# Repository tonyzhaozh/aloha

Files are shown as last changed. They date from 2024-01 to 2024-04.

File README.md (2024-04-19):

# ALOHA: A Low-cost Open-source Hardware System for Bimanual Teleoperation

#### Project Website: https://tonyzhaozh.github.io/aloha/

This codebase contains implementation for teleoperation and data collection with the ALOHA hardware.
To build ALOHA, follow the [Hardware Assembly Tutorial](https://docs.google.com/document/d/1sgRZmpS7HMcZTPfGy3kAxDrqFMtNNzmK-yVtX5cKYME/edit?usp=sharing) and the quick start guide below.
To train imitation learning algorithms, you would also need to install [ACT](https://github.com/tonyzhaozh/act).

### Repo Structure
- ``config``: a config for each robot, designating the port they should bind to, more details in quick start guide.
- ``launch``: a ROS launch file for all 4 cameras and all 4 robots.
- ``aloha_scripts``: python code for teleop and data collection

## Quick start guide

### Hardware selection 

We suggest using a "heavy-duty" computer if possible. 

*In particular, at least 6 USB3 ports are needed. 4 ports for robot connections and 2 ports for cameras.* We have seen cases that a machine was not able to stably connect to all 4 robot arms simultaneously over USB, especially when USB hubs are used.

### Software selection -- OS:

Currently tested and working configurations: 
- :white_check_mark: Ubuntu 18.04 + ROS 1 noetic
- :white_check_mark: Ubuntu 20.04 + ROS 1 noetic

Ongoing testing (compatibility effort underway):
- :construction: ROS 2

### Software installation - ROS:
1. Install ROS and interbotix software following https://docs.trossenrobotics.com/interbotix_xsarms_docs/
2. This will create the directory ``~/interbotix_ws`` which contains ``src``.
3. git clone this repo inside ``~/interbotix_ws/src``
4. ``source /opt/ros/noetic/setup.sh && source ~/interbotix_ws/devel/setup.sh``
5. ``sudo apt-get install ros-noetic-usb-cam && sudo apt-get install ros-noetic-cv-bridge``
6. run ``catkin_make`` inside ``~/interbotix_ws``, make sure the build is successful
7. go to ``~/interbotix_ws/src/interbotix_ros_toolboxes/interbotix_xs_toolbox/interbotix_xs_modules/src/interbotix_xs_modules/arm.py``, find function ``publish_positions``.
   Change ``self.T_sb = mr.FKinSpace(self.robot_des.M, self.robot_des.Slist, self.joint_commands)`` to ``self.T_sb = None``.
   This prevents the code from calculating FK at every step which delays teleoperation.
### Hardware installation:

The goal of this section is to run ``roslaunch aloha 4arms_teleop.launch``, which starts
communication with 4 robots and 4 cameras. It should work after finishing the following steps:

Step 1: Connect 4 robots to the computer via USB, and power on. *Do not use extension cable or usb hub*.
- To check if the robot is connected, install dynamixel wizard [here](https://emanual.robotis.com/docs/en/software/dynamixel/dynamixel_wizard2/)
- Dynamixel wizard is a very helpful debugging tool that connects to individual motors of the robot. It allows
things such as rebooting the motor (very useful!), torque on/off, and sending commands.
However, it has no knowledge about the kinematics of the robot, so be careful about collisions.
The robot *will* collapse if motors are torque off i.e. there is no automatically engaged brakes in joints.
- Open Dynamixel wizard, go into ``options`` and select:
  - Protocal 2.0
  - All ports
  - 1000000 bps
  - ID range from 0-10
- Note: repeat above everytime before you scan.
- Then hit ``Scan``. There should be 4 devices showing up, each with 9 motors.

- One issue that arises is the port each robot binds to can change over time, e.g. a robot that
is initially ``ttyUSB0`` might suddenly become ``ttyUSB5``. To resolve this, we bind each robot to a fixed symlink
port with the following mapping:
  - ``ttyDXL_master_right``: right master robot (master: the robot that the operator would be holding)
  - ``ttyDXL_puppet_right``: right puppet robot (puppet: the robot that performs the task)
  - ``ttyDXL_master_left``: left master robot
  - ``ttyDXL_puppet_left``: left puppet robot
- Take ``ttyDXL_master_right``: right master robot as an example:
  1. Find the port that the right master robot is currently binding to, e.g. ``ttyUSB0``
  2. run ``udevadm info --name=/dev/ttyUSB0 --attribute-walk | grep serial`` to obtain the serial number. Use the first one that shows up, the format should look similar to ``FT6S4DSP``.
  3. ``sudo vim /etc/udev/rules.d/99-fixed-interbotix-udev.rules`` and add the following line: 

         SUBSYSTEM=="tty", ATTRS{serial}=="<serial number here>", ENV{ID_MM_DEVICE_IGNORE}="1", ATTR{device/latency_timer}="1", SYMLINK+="ttyDXL_master_right"

  4. This will make sure the right master robot is *always* binding to ``ttyDXL_master_right``
  5. Repeat with the rest of 3 arms.
- To apply the changes, run ``sudo udevadm control --reload && sudo udevadm trigger``
- If successful, you should be able to find ``ttyDXL*`` in your ``/dev``

Step 2: Set max current for gripper motors
- Open Dynamixel Wizard, and select the wrist motor for puppet arms. The name of it should be ```[ID:009] XM430-W350```
- Tip: the LED on the base of robot will flash when it is talking to Dynamixel Wizard. This will help determine which robot is selected. 
- Find ``38 Current Limit``, enter ``200``, then hit ``save`` at the bottom.
- Repeat this for both puppet robots.
- This limits the max current through gripper motors, to prevent overloading errors.

Step 3: Setup 4 cameras
- You may use usb hub here, but *maximum 2 cameras per hub for reasonable latency*.
- To make sure all 4 cameras are binding to a consistent port, similar steps are needed.
- Cameras are by default binding to ``/dev/video{0, 1, 2...}``, while we want to have symlinks ``{CAM_RIGHT_WRIST, CAM_LEFT_WRIST, CAM_LOW, CAM_HIGH}``
- Take ``CAM_RIGHT_WRIST`` as an example, and let's say it is now binding to ``/dev/video0``. run ``udevadm info --name=/dev/video0 --attribute-walk | grep serial`` to obtain it's serial. Use the first one that shows up, the format should look similar to ``0E1A2B2F``.
- Then ``sudo vim /etc/udev/rules.d/99-fixed-interbotix-udev.rules`` and add the following line 

      SUBSYSTEM=="video4linux", ATTRS{serial}=="<serial number here>", ATTR{index}=="0", ATTRS{idProduct}=="085c", ATTR{device/latency_timer}="1", SYMLINK+="CAM_RIGHT_WRIST"

- Repeat this for ``{CAM_LEFT_WRIST, CAM_LOW, CAM_HIGH}`` in additional to ``CAM_RIGHT_WRIST``
- To apply the changes, run ``sudo udevadm control --reload && sudo udevadm trigger``
- If successful, you should be able to find ``{CAM_RIGHT_WRIST, CAM_LEFT_WRIST, CAM_LOW, CAM_HIGH}`` in your ``/dev``

At this point, have a new terminal
    
    conda deactivate # if conda shows up by default
    source /opt/ros/noetic/setup.sh && source ~/interbotix_ws/devel/setup.sh
    roslaunch aloha 4arms_teleop.launch

If no error message is showing up, the computer should be successfully connected to all 4 cameras and all 4 robots.

#### Trouble shooting
- Make sure Dynamixel Wizard is disconnected, and no app is using webcam's stream. It will prevent ROS from connecting to
these devices.

### Software installation - Conda:

    conda create -n aloha python=3.8.10
    conda activate aloha
    pip install torchvision
    pip install torch
    pip install pyquaternion
    pip install pyyaml
    pip install rospkg
    pip install pexpect
    pip install mujoco==2.3.7
    pip install dm_control==1.0.14
    pip install opencv-python
    pip install matplotlib
    pip install einops
    pip install packaging
    pip install h5py

### Testing teleoperation

**Notice**: Before running the commands below, be sure to place all 4 robots in their sleep positions, and open master robot's gripper. 
All robots will rise to a height that is easy for teleoperation.

    # ROS terminal
    conda deactivate
    source /opt/ros/noetic/setup.sh && source ~/interbotix_ws/devel/setup.sh
    roslaunch aloha 4arms_teleop.launch
    
    # Right hand terminal
    conda activate aloha
    cd ~/interbotix_ws/src/aloha/aloha_scripts
    python3 one_side_teleop.py right
    
    # Left hand terminal
    conda activate aloha
    cd ~/interbotix_ws/src/aloha/aloha_scripts
    python3 one_side_teleop.py left

The teleoperation will start when the master side gripper is closed.

## Example Usages

To set up a new terminal, run:

    conda activate aloha
    cd ~/interbotix_ws/src/aloha/aloha_scripts

The ``one_side_teleop.py`` we ran is for testing teleoperation and has no data collection. To collect data for an episode, run:

    python3 record_episodes.py --dataset_dir <data save dir> --episode_idx 0

This will store a hdf5 file at ``<data save dir>``.
To change episode length and other params, edit ``constants.py`` directly.

To visualize the episode collected, run:

    python3 visualize_episodes.py --dataset_dir <data save dir> --episode_idx 0

To replay the episode collected with real robot, run:

    python3 replay_episodes.py --dataset_dir <data save dir> --episode_idx 0

To lower 4 robots before e.g. cutting off power, run:

    python3 sleep.py

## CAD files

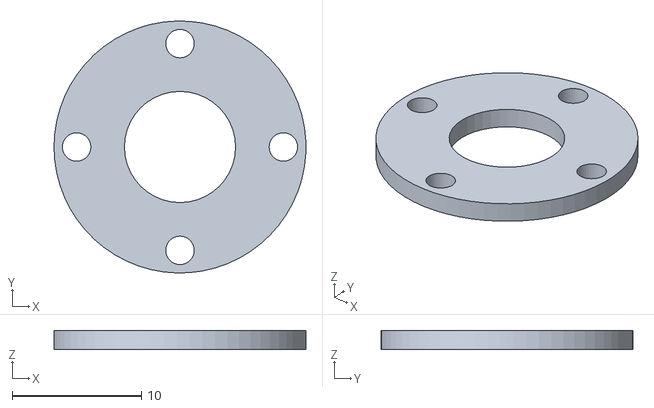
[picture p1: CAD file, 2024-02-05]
aloha2/Shim_rotor_v1.STL
19.5 x 19.5 x 1.50

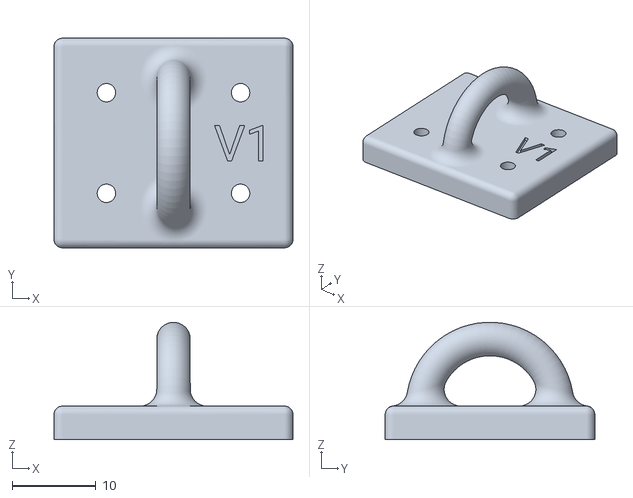
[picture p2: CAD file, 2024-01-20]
aloha2/Gravity compensator clip, elbow mount.stl
28.5 x 25.0 x 14.0

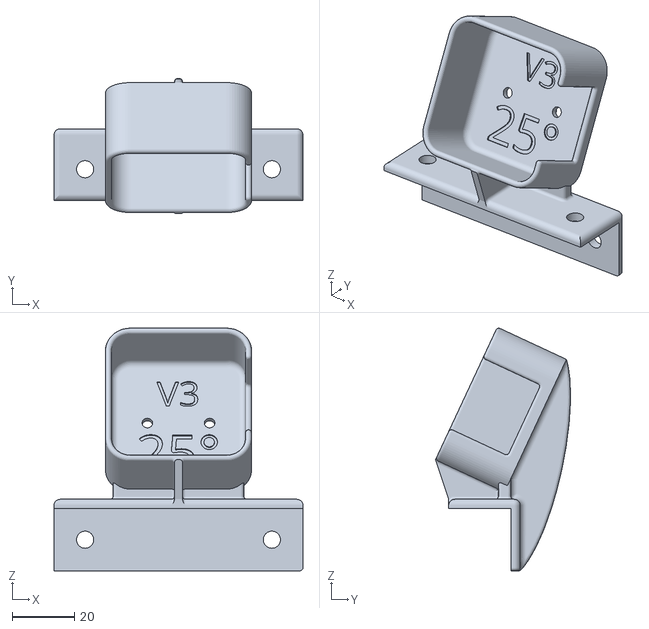
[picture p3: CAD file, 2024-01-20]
aloha2/RSd405 2020 Overhead Cam Mount v3.stl
80.0 x 43.4 x 78.0

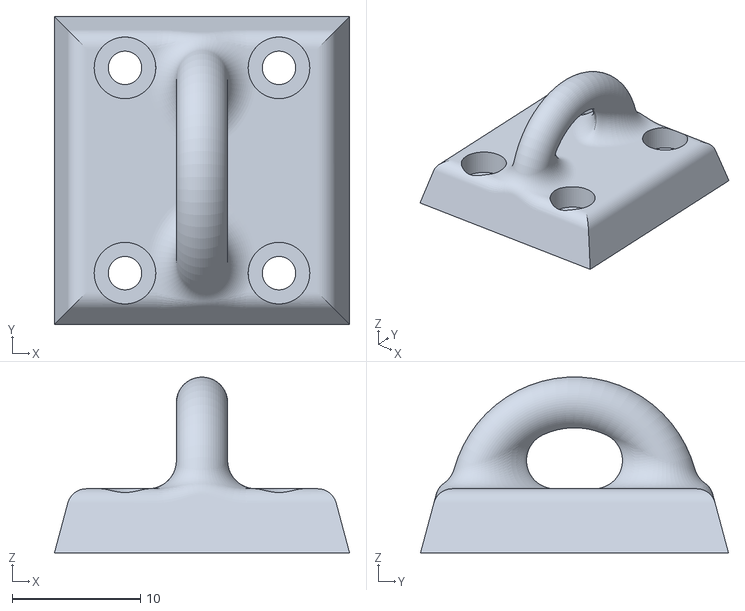
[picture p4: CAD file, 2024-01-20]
aloha2/Gravity compensator clip, wrist mount.stl
23.0 x 24.0 x 13.7

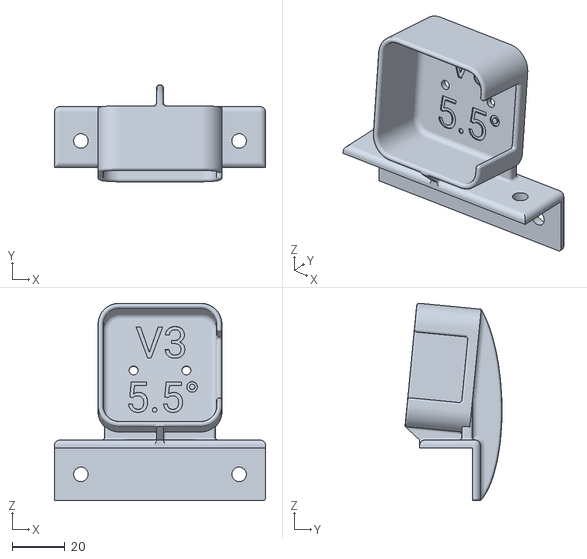
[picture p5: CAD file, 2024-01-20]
aloha2/RSd405 2020 Worms-eye Cam Mount v3.stl
80.0 x 36.8 x 74.9

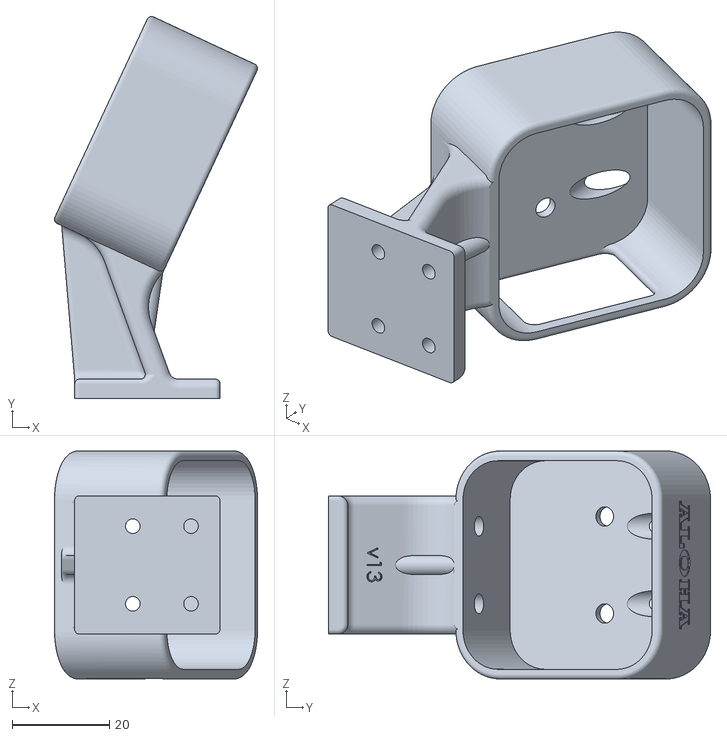
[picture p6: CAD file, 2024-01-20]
aloha2/Aloha cam wrist mount v13.stl
41.9 x 78.8 x 47.0

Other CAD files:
aloha2/W-shim_rotor_v1.STL

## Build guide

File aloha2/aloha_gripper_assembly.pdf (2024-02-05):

# Aloha Gripper Assembly

Version | Date | Author(s) | Description
1.0 | 07/28/23 | Thinh Nguyen

# 1.0 Overview

- This document outlines the steps involved in building the Aloha Gripper.

# 2.0 Parts

WidowX Gripper

Line | Part Description | Supplier | Part # | Qty
1 | W-bridge_rails_support_v1 | STEP FILE | | 1
2 | W-finger_adaptor_v1 | STEP FILE | | 2
3 | W-finger_holder_M_v1 | STEP FILE | | 1
4 | W-gripper_backplate_v1 (acrylic 3mm thickness) | STEP FILE | | 1
5 | W-hand_holder_v1 | STEP FILE | | 1
6 | W-rotor_arm_v1 | STEP FILE | | 2
7 | W-rotor_v1 | STEP FILE | | 1
8 | W-shim_rotor_v1 | STEP FILE | | 1
9 | 6725K27_5 mm Wide x 120 mm Long Rail Ball Bearing Carriage | McMaster | 6725K23 (https://www.mcmaster.com/6725K23-6725K27/) | 1
10 | 8438K1_Corrosion-Resistant Ball Bearing Carriage | McMaster | 8438K1 (https://www.mcmaster.com/8438K1/) | 4
11 | Deep Groove Ball Bearing (3mmx6mmx2.5mm) | Amazon | Amazon (https://www.amazon.com/gp/product/B075CMRGY6/ref=ppx_yo_dt_b_asin_image_o01_s00?ie=UTF8&psc=1) | 6
12 | M2 Brass Male-Female / Female-Female | Amazon | Amazon (https://www.amazon.com/gp/product/B07ZSZW8T1/ref=ppx_yo_dt_b_asin_title_o05_s00?ie=UTF8&psc=1) | 1
13 | Flat Head Screw M3 x 0.5 mm Thread, 10 mm Long | McMaster | 92125A130 (https://www.mcmaster.com/92125A130/) | 4
14 | Flat Head Screw M3 x 0.5 mm Thread, 20 mm Long | McMaster | 92125A136 (https://www.mcmaster.com/92125A136/) | 2
15 | Flat Head Screw M2 x 0.4 mm Thread, 10 mm Long | McMaster | 92010A005 (https://www.mcmaster.com/92010A005/) | 22

16 | Flat Head Screw M2 x 0.4 mm Thread, 16 mm Long | McMaster | 92010A008 (https://www.mcmaster.com/92010A008/) | 4
17 | Flat Head Screw M2 x 0.4 mm Thread, 20 mm Long | McMaster | 92095A106 (https://www.mcmaster.com/92095A106/) | 6
18 | Socket Head Screw M2 x 0.4 mm Thread, 6 mm Long | McMaster | 91292A831 (https://www.mcmaster.com/91292A831/) | 2
19 | Hex Nut M2 x 0.4 mm Thread | McMaster | 91828A111 (https://www.mcmaster.com/91828A111/) | 16
20 | Flat Head Screw M2.5 x 0.45 mm Thread, 16 mm Long | McMaster | 93395A185 (https://www.mcmaster.com/93395A185/) | 4
21 | Steel Washer for M2 Screw Size, 2.200 mm ID, 4.500 mm OD | McMaster | 98688A110 (https://www.mcmaster.com/98688A110/) | 8
22 | Short profile button head m2 x6mm (come with rails) | | | 8
23 | M3 Steel Nylon-Insert Locknut | McMaster | 90576A102 (https://www.mcmaster.com/90576A102/) | 2
24 | Socket Head Screw M2.5 x 0.45 mm Thread, 8 mm Long | McMaster | 91292A012 (https://www.mcmaster.com/91292A012/) | 8

Viper Gripper

Line | Part Description | Supplier | Part # | Qty
1 | Bridge_rails_support_v1 | STEP FILE | | 1
2 | Finger_adaptor_v1 | STEP FILE | | 2
3 | Finger_v1 | STEP FILE | | 1
4 | Gripper_backplate_v1(acrylic 3mm thickness) | STEP FILE | | 1
5 | Rotor_arm_v1 | STEP FILE | | 2
6 | Rotor_v1 | STEP FILE | | 1
7 | Shim_rotor_v1 | STEP FILE | | 1
8 | 6725K27_5 mm Wide x 150 mm Long Rail Ball Bearing Carriage | McMaster | 6725K23 (https://www.mcmaster.com/6725K23-6725K28/) | 1
9 | 8438K1_Corrosion-Resistant Ball Bearing Carriage | McMaster | 8438K1 (https://www.mcmaster.com/8438K1/) | 4
10 | Deep Groove Ball Bearing (3mmx6mmx2.5mm) | Amazon | Amazon (https://www.amazon.com/gp/product/B075CMRGY6/ref=ppx_yo_dt_b_asin_image_o01_s00?ie=UTF8&psc=1) | 6
11 | M2 Brass Male-Female / Female-Female | Amazon | Amazon (https://www.amazon.com/gp/product/B07ZSZW8T1/ref=ppx_yo_dt_b_asin_title_o05_s00?ie=UTF8&psc=1) | 1
12 | Flat Head Screw M3 x 0.5 mm Thread, 10 mm Long | McMaster | 92125A130 (https://www.mcmaster.com/92125A130/) | 4
13 | Flat Head Screw M3 x 0.5 mm Thread, 20 mm Long | McMaster | 92125A136 (https://www.mcmaster.com/92125A136/) | 2
14 | Flat Head Screw M2 x 0.4 mm Thread, 10 mm Long | McMaster | 92010A005 (https://www.mcmaster.com/92010A005/) | 22
15 | Flat Head Screw M2 x 0.4 mm Thread, 16 mm Long | McMaster | 92010A008 (https://www.mcmaster.com/92010A008/) | 4
16 | Flat Head Screw M2 x 0.4 mm Thread, 20 mm Long | McMaster | 92095A106 (https://www.mcmaster.com/92095A106/) | 6
17 | Socket Head Screw M2 x 0.4 mm Thread, 6 mm Long | McMaster | 91292A831 (https://www.mcmaster.com/91292A831/) | 2
18 | Hex Nut M2 x 0.4 mm Thread | McMaster | 91828A111 (https://www.mcmaster.com/91828A111/) | 16
19 | Flat Head Screw M2.5 x 0.45 mm Thread, 16 mm Long | McMaster | 93395A185 (https://www.mcmaster.com/93395A185/) | 4
20 | Steel Washer for M2 Screw Size, 2.200 mm ID, 4.500 mm OD | McMaster | 98688A110 (https://www.mcmaster.com/98688A110/) | 8
21 | Short profile button head m2 x6mm (come with rails) | | | 8
22 | M3 Steel Nylon-Insert Locknut | McMaster | 90576A102 (https://www.mcmaster.com/90576A102/) | 2

# 3.0 Assembly

## 3.1 Mechanical

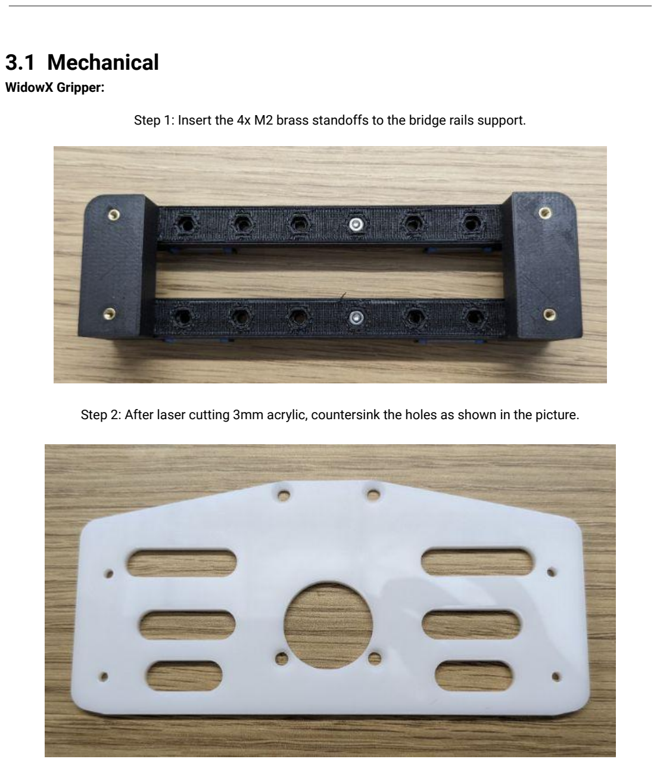
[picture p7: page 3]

WidowX Gripper:

Step 1: Insert the 4x M2 brass standoffs to the bridge rails support.
Step 2: After laser cutting 3mm acrylic, countersink the holes as shown in the picture.

Step 3: Install the 3 bearings on the rotor arm (2 on the right side and 1 on the left side).

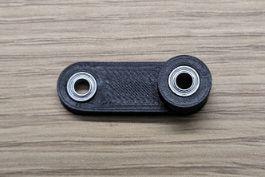
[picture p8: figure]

Step 4: Use a tap to create M3 threads in the middle holes, to a depth of about 5mm.

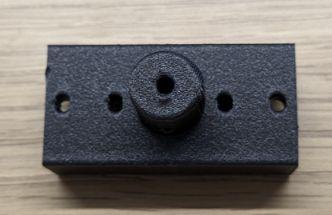
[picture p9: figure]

Step 5: Attach the rotor and rotor arm together with an M3x10mm countersunk screw and lock nut, as shown in the figure.

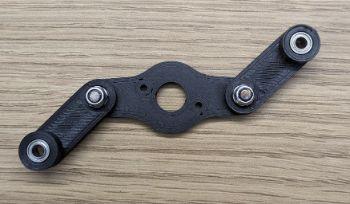
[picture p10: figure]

Step 6: Attach the rails with carriages to the bridge, and secure them with M2x16mm countersunk screws at both ends. Use M2 x 10mm countersunk screws and nuts to secure the middle holes.

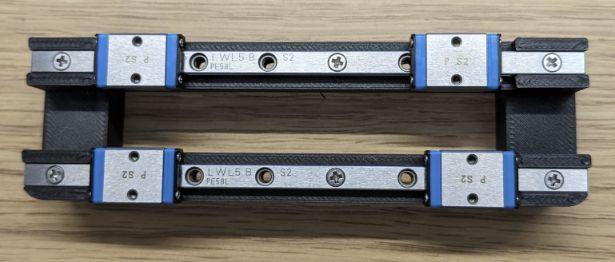
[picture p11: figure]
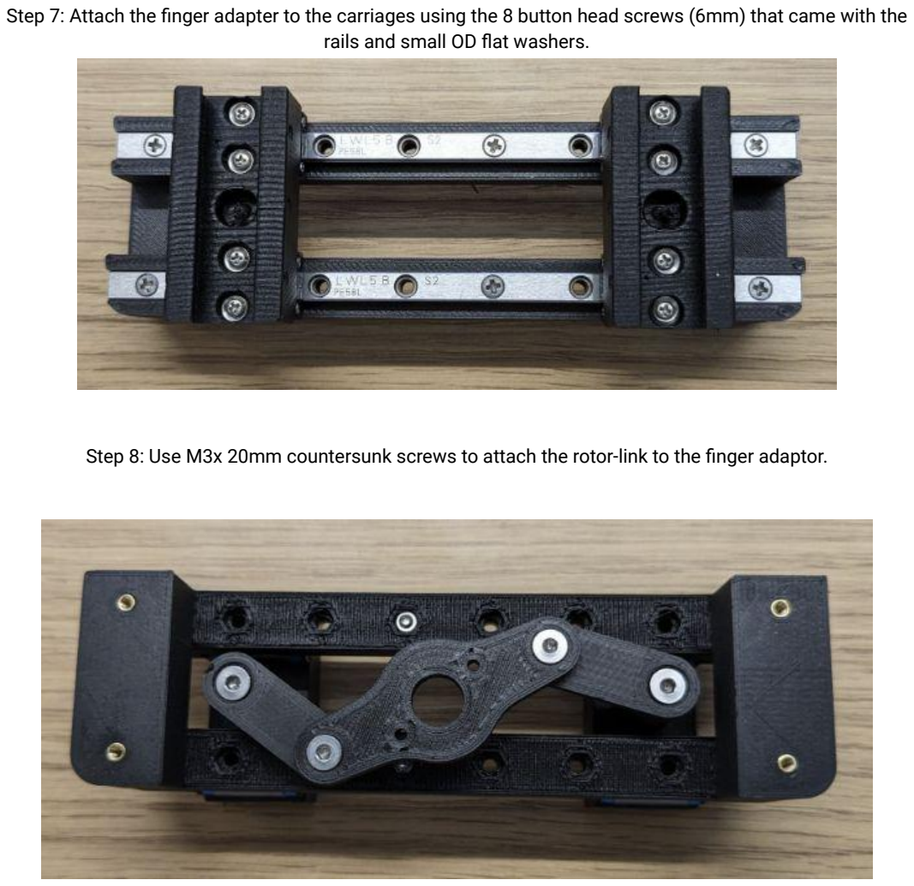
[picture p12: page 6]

Step 7: Attach the finger adapter to the carriages using the 8 button head screws (6mm) that came with the rails and small OD flat washers.
Step 8: Use M3x 20mm countersunk screws to attach the rotor-link to the finger adaptor.

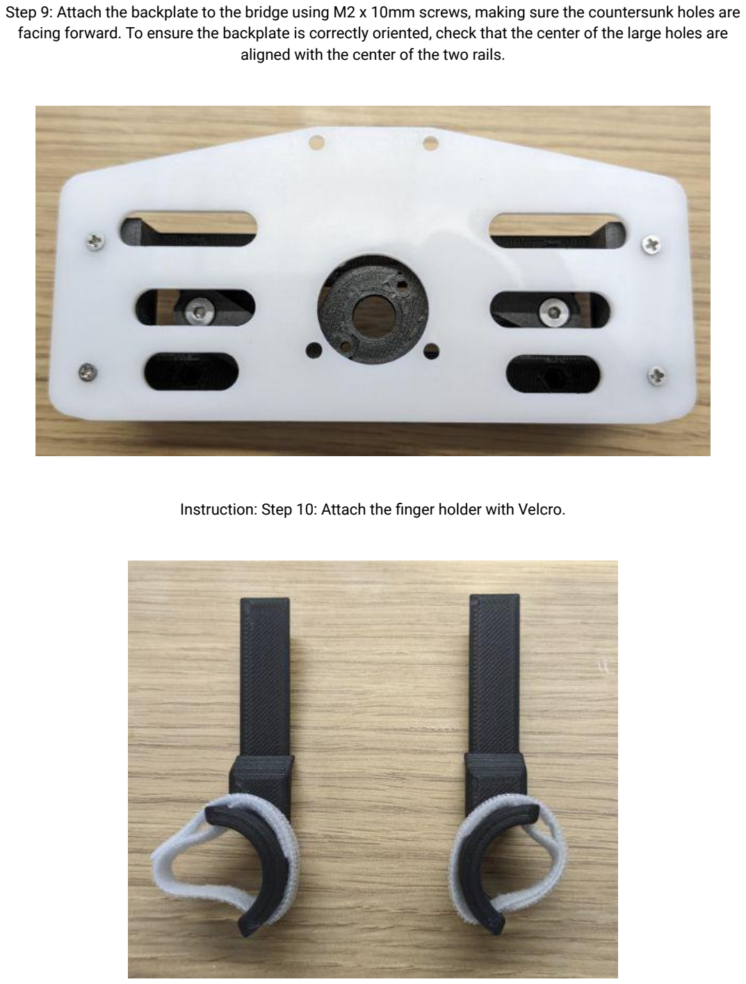
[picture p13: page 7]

Step 9: Attach the backplate to the bridge using M2 x 10mm screws, making sure the countersunk holes are facing forward. To ensure the backplate is correctly oriented, check that the center of the large holes are aligned with the center of the two rails.

Instruction: Step 10: Attach the finger holder with Velcro.

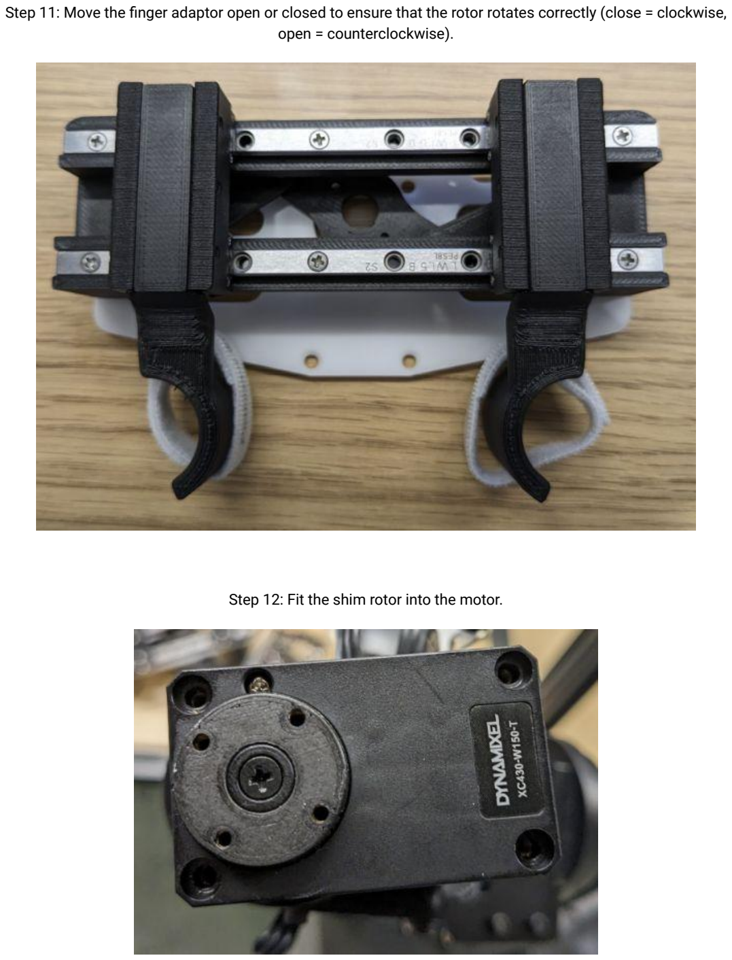
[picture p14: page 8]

Step 11: Move the finger adaptor open or closed to ensure that the rotor rotates correctly (close = clockwise, open = counterclockwise).
Step 12: Fit the shim rotor into the motor.

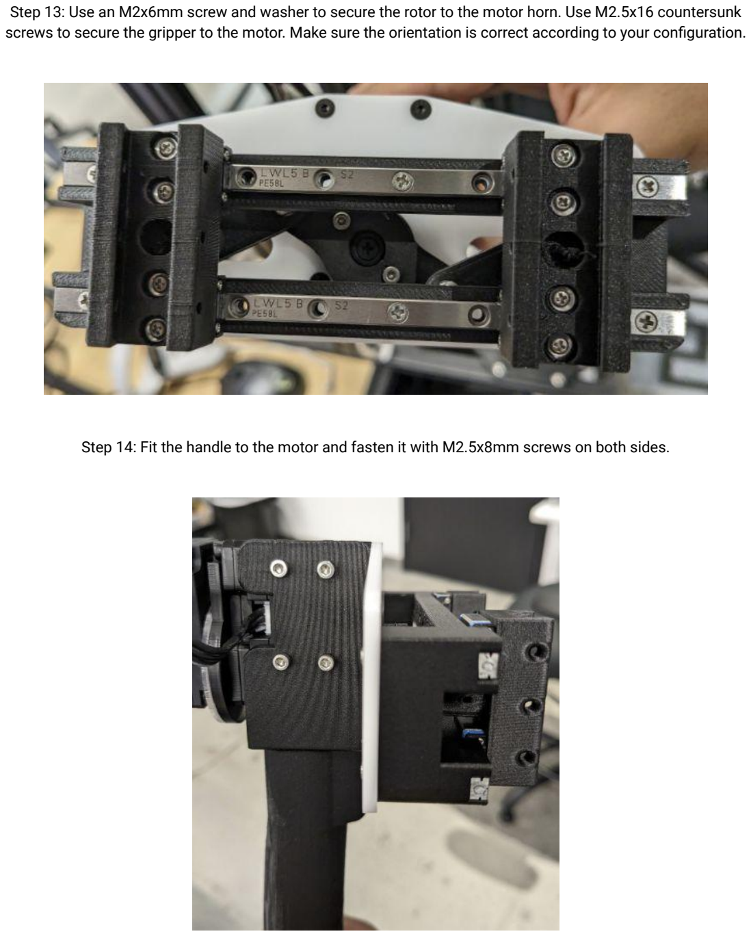
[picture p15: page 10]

Step 13: Use an M2x6mm screw and washer to secure the rotor to the motor horn. Use M2.5x16 countersunk screws to secure the gripper to the motor. Make sure the orientation is correct according to your configuration.
Step 14: Fit the handle to the motor and fasten it with M2.5x8mm screws on both sides.

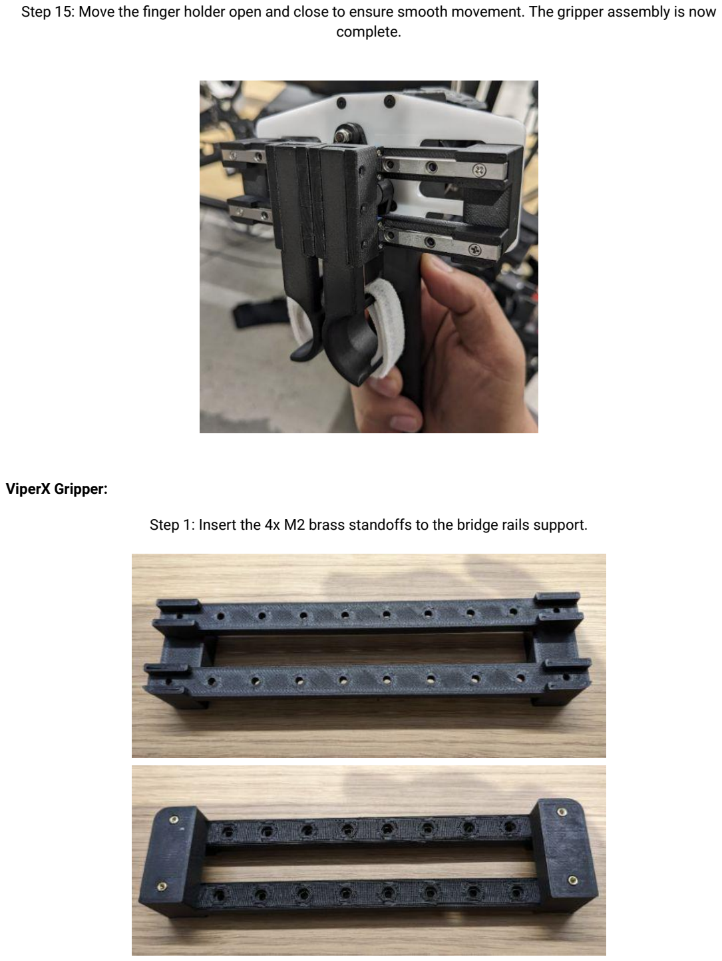
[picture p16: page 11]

Step 15: Move the finger holder open and close to ensure smooth movement. The gripper assembly is now complete.

ViperX Gripper:

Step 1: Insert the 4x M2 brass standoffs to the bridge rails support.

Step 2: After laser cutting 3mm acrylic, countersink the holes as shown in the picture.

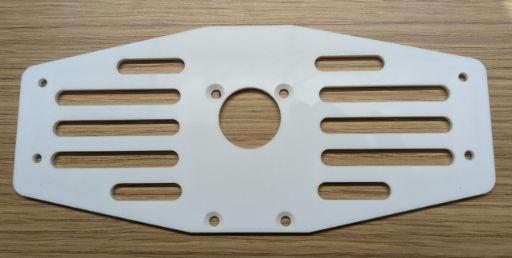
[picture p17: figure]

Step 3: Install the 3 bearings on the rotor arm (2 on the left side and 1 on the right side).

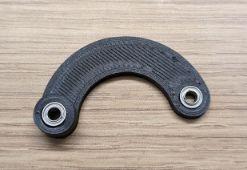
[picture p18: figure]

Step 4: Use a tap to create M3 threads in the middle holes, to a depth of about 5mm.

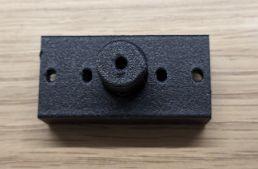
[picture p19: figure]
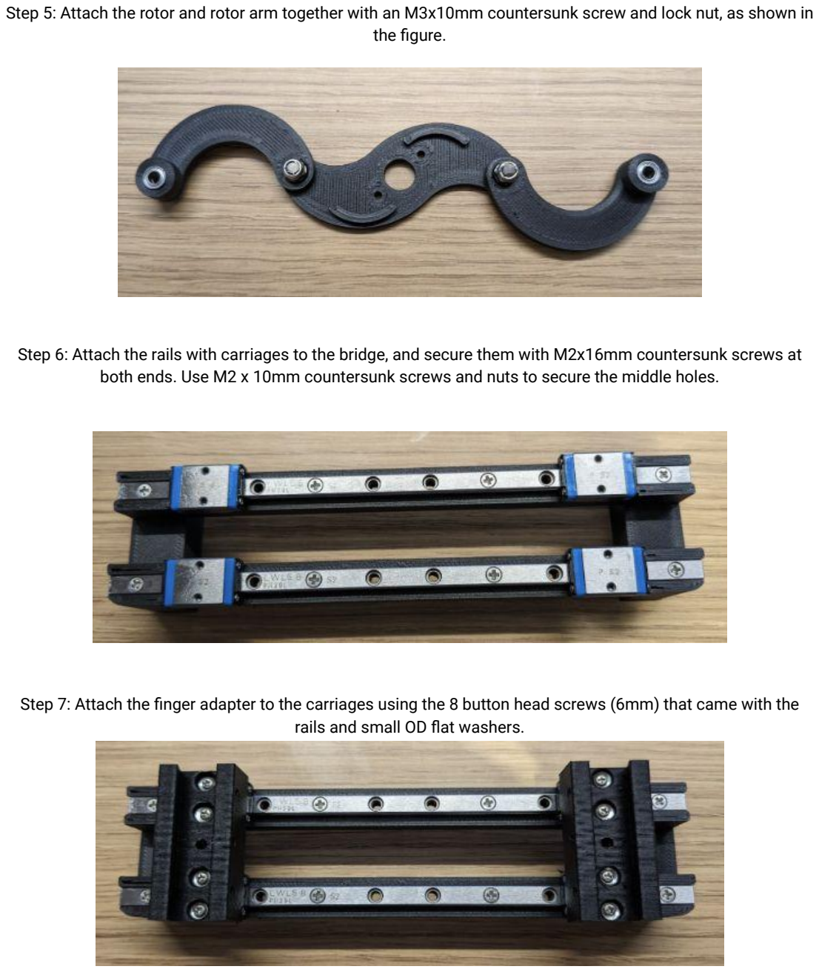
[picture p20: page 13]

Step 5: Attach the rotor and rotor arm together with an M3x10mm countersunk screw and lock nut, as shown in the figure.
Step 6: Attach the rails with carriages to the bridge, and secure them with M2x16mm countersunk screws at both ends. Use M2 x 10mm countersunk screws and nuts to secure the middle holes.
Step 7: Attach the finger adapter to the carriages using the 8 button head screws (6mm) that came with the rails and small OD flat washers.

Step 8: Use M3x 20mm countersunk screws to attach the rotor-link to the finger adaptor.

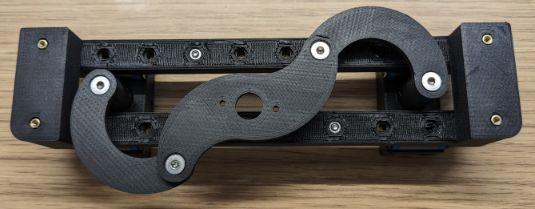
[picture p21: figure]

Step 9: Attach the backplate to the bridge using M2 x 10mm screws, making sure the countersunk holes are facing forward. To ensure the backplate is correctly oriented, check that the center of the large holes are aligned with the center of the two rails.

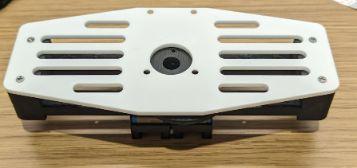
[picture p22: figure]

Step 10: Move the finger adaptor open or closed to ensure that the rotor rotates correctly (close = clockwise, open = counterclockwise).

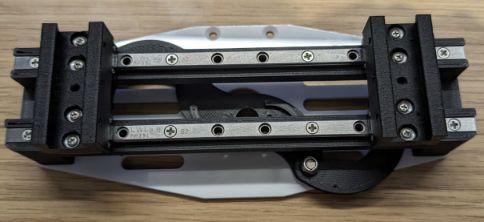
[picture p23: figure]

Step 11: Attach the fabric tab to the finger.

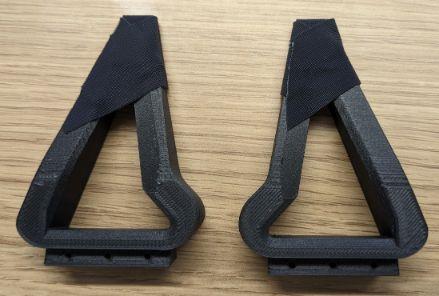
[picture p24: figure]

Step 12: Slide the finger-to-finger adapter into place and secure it with M2x 20mm screws.

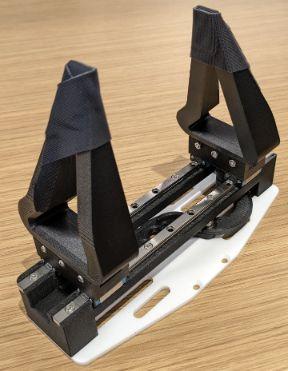
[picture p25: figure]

Step 13: Fit the shim rotor into the motor.

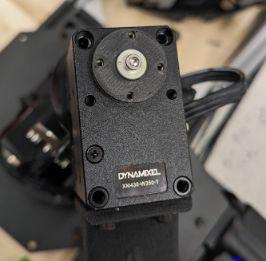
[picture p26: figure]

Step 14: Use an M2x6mm screw and washer to secure the rotor to the motor horn. Use M2.5x16 countersunk screws to secure the gripper to the motor. Make sure the orientation is correct according to your configuration.

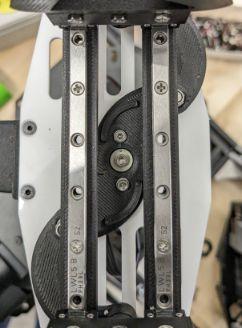
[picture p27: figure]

Step 15: Move the finger open and close to ensure smooth movement. The gripper assembly is now complete.

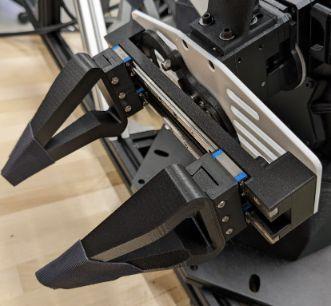
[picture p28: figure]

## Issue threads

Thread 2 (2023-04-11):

### ISSUE TITLE
May I ask whether this system is understood as an anti-interference teaching device？

### ISSUE THREAD

**Issue by haxx12113** [tonyzhaozh/aloha#2]
Hello, may I ask that this system can cope with interference, but there is no introduction of reinforcement learning in the paper, may I ask whether this is similar to the teaching device to demonstrate the playback of objects in accordance with the original teaching Angle? Instead of learning how to tie your shoes, play ping-pong, and thread in different directions?

**Comment by tonyzhaozh** [comment]
Yes this setup is designed for imitation learning (a more general "playback"). While it is certainly possible to run RL on ALOHA.

**Comment by ronjian** [comment]
Is it possible to train the model on the dataset which is collected from the camera+IMU device mounted on human arm?

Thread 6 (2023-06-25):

### ISSUE TITLE
How to set the current limit on a gripper using python api

### ISSUE THREAD

**Issue by DuaneNielsen** [tonyzhaozh/aloha#6]
Hey Tony,

Not an issue, feel free to close when you see it...

I read a comment in your code that you were trying to figure out how to set the current limit.

I chanced upon the solution, below...

I think you can get or set any register on the dynamixels using these ros services...

```
#!/usr/bin/env python

import rospy
from interbotix_xs_msgs.srv import RegisterValues


def service_command(service_path, cmd_type, name, reg, value=0):
    rospy.wait_for_service(service_path)

    try:
        get_registers = rospy.ServiceProxy(service_path, RegisterValues)

        # Make the service call
        response = get_registers(cmd_type, name, reg, value)

        # Process the response
        if response:
            print("Register values: ", response.values)
        else:
            print("Failed to get register values.")

    except rospy.ServiceException as e:
        print("Service call failed:", str(e))




if __name__ == '__main__':
    rospy.init_node('gripper_register_node')
    service_command('/puppet_left/get_motor_registers', 'single', 'gripper', 'Current_Limit')
    service_command('/puppet_left/set_motor_registers', 'single', 'gripper', 'Current_Limit', 800)
    service_command('/puppet_left/get_motor_registers', 'single', 'gripper', 'Current_Limit')
```

there is an equivalent ros command also, the form is something like...

```
rosservice call /puppet_left/get_motor_registers single gripper Hardware_Error_Status 0
```

**Comment by LSinterbotix** [comment]
You could also set `Current_Limit` (along with any other register EEPROM or RAM) on startup using a robot's [motor_config file](https://docs.trossenrobotics.com/interbotix_xsarms_docs/ros_interface/ros1/overview/xs_sdk.html#motor-configs-param-ros1).

For example, if you wanted to set `Current_Limit` on the ViperX-300s gripper motor, you would modify the [vx300s motor config](https://github.com/Interbotix/interbotix_ros_manipulators/blob/main/interbotix_ros_xsarms/interbotix_xsarm_control/config/vx300s.yaml) file like so:

```diff
  gripper:
    ID: 9
    Baud_Rate: 3
    Return_Delay_Time: 0
    Drive_Mode: 0
    Velocity_Limit: 131
    Min_Position_Limit: 0
    Max_Position_Limit: 4095
    Secondary_ID: 255
+   Current_Limit: 800
```

**Comment by DuaneNielsen** [comment]
Also, here's another way to set a motor register on the gripper, using the Interbotix python API

```
puppet_bot = InterbotixManipulatorXS(robot_model="vx300s", group_name="arm", gripper_name="gripper", robot_name=f'puppet_{robot_side}', init_node=True)
puppet_bot.gripper.core.srv_set_reg('single', 'gripper', 'Current_Limit', 500)
```

Also, after using the robot and studying the API a bit more... I suspect you may have been intending to set the "Goal_Current" and not the "Current_Limit".  

When operating mode is "Current-based Position Control Mode", The "Goal_Current" register, will cause the gripper motor to limit the amount of current it uses.  This will ensure that the gripper motor applies no more than a maximum amount of torque to an object when it squeezes it.

"Current_Limit" will cause the motor to go into "Overload" state, reduce torque to zero and stop responding to further commands when more than the set amount of current is detected for a period of time.

So if we set Current_Limit to 300, we probably also should set the Goal_Current to a little less than 300.

I'm currently updating my clone with this config.  Let me know if this make sense to you.  Happy to send a PR if it turns out to be useful.

**Comment by MindFactoryAI** [comment]
Update to this one.  Here is how I'm currently setting the grippers, using the interbotix API...

puppet_bot = InterbotixManipulatorXS(robot_model="vx300s", group_name="arm", gripper_name="gripper",robot_name=f'puppet_{robot_side}', init_node=True)

The order of operations turns out to be important.

First we reboot the motors.
Then disable torque so we can set the current limit
Then set the current limit
Then set current based position mode.

I learned when current based position mode is set, torque will automatically be turned on.  So you cant set the operating mode then set the parameters.  You have to do the operations in the below order...

```
def reboot_grippers(puppet_bot_left, puppet_bot_right, current_limit=1000):

    for bot in [puppet_bot_left, puppet_bot_right]:
        bot.dxl.robot_reboot_motors("single", "gripper", True)
        bot.dxl.robot_torque_enable("single", "gripper", False)
        bot.dxl.robot_set_motor_registers("single", "gripper", 'Current_Limit', current_limit)
        bot.dxl.robot_set_operating_modes("single", "gripper", "current_based_position")
        bot.dxl.robot_torque_enable("single", "gripper", True)
```

**Comment by MindFactoryAI** [comment]
Also, I did some testing of the gripper motors, and as you mention in your instructions, setting current_limit to higher values than 300 causes overloading, even in current_based_position mode.  Whereas if it's set to 300, I observe no overloading.  Anyone reading this thread can verify this by placing an object in the gripper, then closing it using the dynamixel wizard with various current_limits.

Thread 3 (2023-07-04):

### ISSUE TITLE
conda python version 3.8.16 libffi error

### ISSUE THREAD

**Issue by DuaneNielsen** [tonyzhaozh/aloha#3]
Hey Tony,

Latest 3.8.16 version of python is broken on Ubuntu 20.04

will give the below error.. (when executing recording.py)

```
cv_bridge.boost.cv_bridge_boost import getCvType
ImportError: /lib/x86_64-linux-gnu/libp11-kit.so.0: undefined symbol: ffi_type_pointer, version LIBFFI_BASE_7.0
```

This is due to an incompatibility between the libffi shipped with 20.04, and the version python 3.8.16 expects..  ( think it's 3.3 in 20.04 but python is expecting 3.4... something like that)

```
conda install python=3.8.10
```

in the aloha environment fixes the problem.

Recommend specifying 3.8.10 in the README.md instead of 3.8 as current

**Comment by tonyzhaozh** [comment]
Hi Duane,

Sorry for the late reply as I have been quite busy lately. I actually encountered the same error when installing Aloha in a new computer, and have been quite perplexed by it. Looks like this is the root cause and thanks for catching it!

I just updated the requirement [here](https://github.com/tonyzhaozh/aloha/commit/f3306d42e800b6d486c309bebf316fe06103e86b).

Aloha,
Tony

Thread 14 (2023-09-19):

### ISSUE TITLE
What if the policy network without CVAE?

### ISSUE THREAD

**Issue by ManUtdMoon** [tonyzhaozh/aloha#14]
Hey Tony,

Thank you for your great work!

I have a question about the policy network selection. I noticed that in order to consider the stochasity of human demonstrations, you choose to leverage CVAE to model the action distribution, which outperforms the method w/o CVAE in the ablation study.

I wonder whether the policy without CVAE is identical to a distributional policy. What if the mean and covariance are both learned during training? To this end, will introducing policy entropy into a distributional  policy w/o CVAE work?

Thank you for your time. I am looking forward to your reply :D

Regards,
Dongjie

**Comment by tonyzhaozh** [comment]
Hi Dongjie,

Not sure if I completely understand your comment, but are you referring to a policy that outputs mean and covariance of the action? That could work theoretically, but its hard in the case of chunking to predict a sequence of actions and a full covariance matrix, as the latter one will be too high dimensional.

In addition, we recently noticed that the CVAE might not matter much. You can try training a policy without the CVAE encoder and latent code, and it might work similarly. We are still investigating more on this and potentially update the original paper.

Thanks,
Tony

**Comment by ManUtdMoon** [comment]
Hi Tony,

Thank you for your reply and it answers my questions. Looking forward to your updates on more effecitive policy architectures.

Regards,
Dongjie

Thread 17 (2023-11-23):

### ISSUE TITLE
Please set the gripper's 'operating mode' to 'pwm' or 'current'

### ISSUE THREAD

**Issue by onePnot1** [tonyzhaozh/aloha#17]
Hi,

When I run `roslaunch aloha 4arms_teleop.launch`, I get four errors like `Please set the gripper's 'operating mode' to 'pwm' or 'current'`

Should I solve them or just ignore?

**Comment by sp-sophia-labs** [comment]
Hi, 

I have the same error after following the README. On my side it shows when running any execution script on the ALOHA. `python3 record_episodes.py` or `python3 one_side_teleop.py`. I have these two errors `Please set the group's 'profile type' to 'time'.` and `Please set the gripper's 'operating mode' to 'pwm' or 'current'.` triggering for each of the robots

I've been ignoring the issues with no problem so far

**Comment by onePnot1** [comment]
> Hi,
> 
> I have the same error after following the README. On my side it shows when running any execution script on the ALOHA. `python3 record_episodes.py`, `python3 one_side_teleop.py` or `python3 sleep.py`. I have these two errors `Please set the group's 'profile type' to 'time'.` and `Please set the gripper's 'operating mode' to 'pwm' or 'current'.` triggering for each of the robots
> 
> I have been ignoring these errors with no problem so far

Thanks a lot.

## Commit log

2024-01-20 Added gravity comp mounts, and updated wrist cam mounts.
    [Aloha cam wrist mount v13.stl, Gravity compensator clip, elbow mount.stl, Gravity compensator clip, wrist mount.stl, RSd405 2020 Overhead Cam Mount v3.stl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]
2024-02-05 Update name of hardware folder to aloha2
    [Aloha cam wrist mount v13.stl, Gravity compensator clip, elbow mount.stl, Gravity compensator clip, wrist mount.stl, RSd405 2020 Overhead Cam Mount v3.stl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]
2024-04-18 Update README.md
    max current 300 -> 200 (to match actual usage).
